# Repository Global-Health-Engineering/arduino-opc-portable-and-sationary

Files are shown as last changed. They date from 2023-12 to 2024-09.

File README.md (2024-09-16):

# Portable and Stationary PM Monitors using Arduino UNO and Alphasense OPC-N3

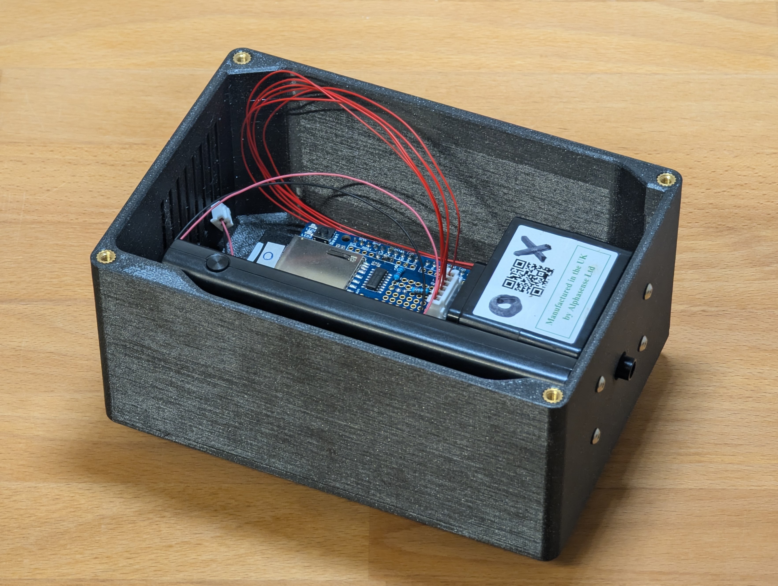
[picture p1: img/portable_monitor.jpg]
portable_monitor


## 1. Overview

This repository provides instructions for the building of particulate matter monitoring systems using the Arduino UNO and Alphasense OPC-N3 optical particle counter module.

There are two variants:

- A portable monitor to measure the personal exposure to particulate matter.
- A stationary monitor for remote long(er)-term deployment.

This repository is part of a bachelor's thesis whose goal it was to develope adaptable low-cost PM monitors and provide a simple and free guide for others also looking to build such systems. The monitors described in this repository can either be copied directly or used as the basis for custom units adapted to specific needs. The project itself is licensed under the the [`CC-BY 4.0`](LICENSE.md) license, however some of the software libraries used are come with different licenses. For more details on this, see [`Section 3`](#3-software-library-licensing) of this README file.

### 1.1. System Overview

The core of both the portable and stationary monitors is a stack made up of an Arduino UNO and an Adafruit Data Logger Shield (DLS). The stationary monitor also includes a DFRobot SIM7600CE-T shield for wireless data transmission to Google Drive. Both monitors feature local data storage on an SD card and proper timestamping using the DLS' real-time clock. To interface with the Alphasense OPC-N3 module, a voltage divider is required to drop the SPI lines from 5 V to 3 V. The handy prototyping area of the DLS is used to implement this and also to host all of the required connectors for power, communication and (optional) status LEDs.

--TODO IMAGE_PORTABLE_SCHEMATIC_OVERVIEW

--TODO IMAGE_STATIONARY_SCHEMATIC_OVERVIEW

### 1.2. Cost breakdown

One goal of the project was to keep the cost of the monitors low, so they are built from readily available and affordable components. The only real exception is the Alphasense OPC-N3. This is rather pricey but could be substituted by a cheaper sensor module if not all of its particular functionality is needed (be aware, replacing the OPC migth require changing the hardware and software interface).

The following tables give a rough breakdown of the costs of each of the monitors. The links are for reference only as sourcing the parts locally is most likely the cheapest option!

#### Cost breakdown of the portable monitor.

| Name                                   | Source                                                                                                         | Approx. price (CHF)    |
| -------------------------------------- | -------------------------------------------------------------------------------------------------------------- | ---------------------: |
| Arduino UNO (R3/R4 Minima)             | [Mouser](https://www.mouser.ch/ProductDetail/Arduino/ABX00080?qs=ulEaXIWI0c9tbG%2FHj5EzRA%3D%3D)               | 20.-                   |
| Adafruit Data Logger Shield (Rev. C)   | [Mouser](https://www.mouser.ch/ProductDetail/Adafruit/1141?qs=GURawfaeGuAe9uOWyGs1aw%3D%3D)                    | 15.-                   |
| SD card (32 GB)                        | [Mouser](https://www.mouser.ch/ProductDetail/SanDisk/SDSDAA-032G?qs=EgF7oUuTQmpUPFrDZtLtsQ%3D%3D)              | 20.-                   |
| RTC battery (CR1220)                   | [Digitec](https://www.digitec.ch/en/s1/product/energizer-cr1220-lithium-1-pcs-cr1220-40-mah-batteries-8762860) | 5.-                    |
| Powerbank                              | [Digitec](https://www.digitec.ch/en/s1/product/sbs-power-bank-10000-mah-5-w-37-wh-powerbanks-19791017)         | 35.-                   |
| Alphasense OPC-N3                      | N/A                                                                                                            | ~500.-                 |
| Small components (LEDs, resistors, wires, etc.) | N/A                                                                                                   | ~10.-                  |
| **Total**                              |                                                                                                                | ~570.-                 |

#### Cost breakdown of the stationary monitor.

| Name                                   | Source                                                                                                                        | Approx. price (CHF)    |
| -------------------------------------- | ----------------------------------------------------------------------------------------------------------------------------- | ---------------------: |
| Arduino UNO (R3/R4 Minima)             | [Mouser](https://www.mouser.ch/ProductDetail/Arduino/ABX00080?qs=ulEaXIWI0c9tbG%2FHj5EzRA%3D%3D)                              | 20.-                   |
| Adafruit Data Logger Shield (Rev. C)   | [Mouser](https://www.mouser.ch/ProductDetail/Adafruit/1141?qs=GURawfaeGuAe9uOWyGs1aw%3D%3D)                                   | 15.-                   |
| SD card (32 GB)                        | [Mouser](https://www.mouser.ch/ProductDetail/SanDisk/SDSDAA-032G?qs=EgF7oUuTQmpUPFrDZtLtsQ%3D%3D)                             | 20.-                   |
| RTC battery (CR1220)                   | [Digitec](https://www.digitec.ch/en/s1/product/energizer-cr1220-lithium-1-pcs-cr1220-40-mah-batteries-8762860)                | 5.-                    |
| Alphasense OPC-N3                      | N/A                                                                                                                           | ~500.-                 |
| UPS board                              | Aliexpress                                                                                                                    | ~5.-                   |
| UPS batteries (2x 18650)               | [Digitec](https://www.digitec.ch/en/s1/product/samsung-lithium-ion-battery-type-18650-1-pcs-18650-285-mah-batteries-16208254) | 30.-                   |
| DFRobot SIM7600CE-T                    | [Mouser](https://www.mouser.ch/ProductDetail/DFRobot/TEL0124?qs=17u8i%2FzlE88MEbXRJuYFsA%3D%3D)                               | 60.-                   |
| Small components (LEDs, resistors, wires, etc.) | N/A                                                                                                                  | ~15.-                  |
| **Total**                              |                                                                                                                               | ~670.-                 |

The cost breakdowns do **NOT** include housings for the monitors, as this is very dependant on the exact use case. They could be as simple as a plastic food container. For this project, the housings were 3D-printed on a consumer grade FDM printer. More details on these can be found in [`Section 1.3.`](#13-3d-printed-housings) of this README file.

### 1.3. 3D-Printed Housings

The files for the 3D-printed housings can be found in the [`cad`](cad) directory. This also contains some simplified CAD models of the UNO and OPC to allow you to design your own housings.

The designs provided can be printed on standard consuer grade FDM printers. They should be printed from a material such as PETG or ASA to make sure they are strong enough and not easily damaged by UV radiation.

#### 1.3.1. Portable Monitor Housing

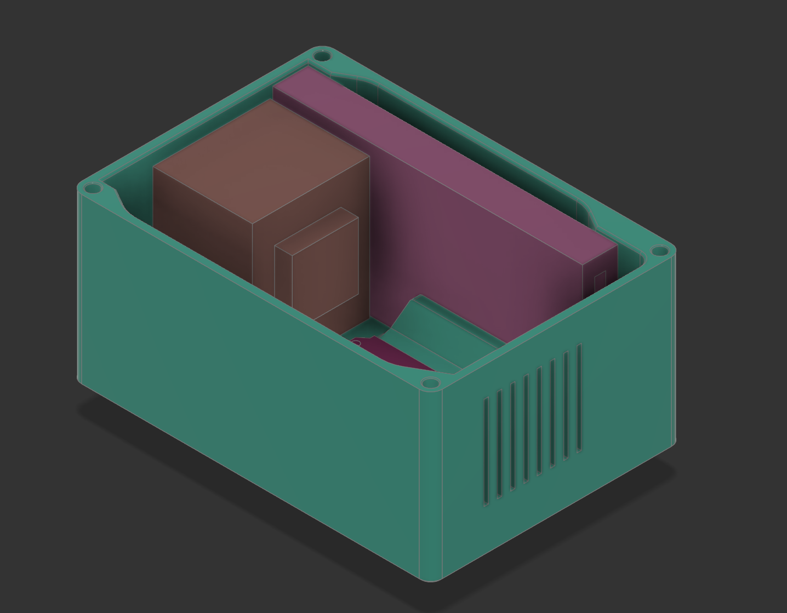
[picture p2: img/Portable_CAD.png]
Portable housing


The housing for the portabel monitor is designed to be used with a GoPro 'Chesty' chest harness. This allows the monitor to be worn somewhat comfortably.

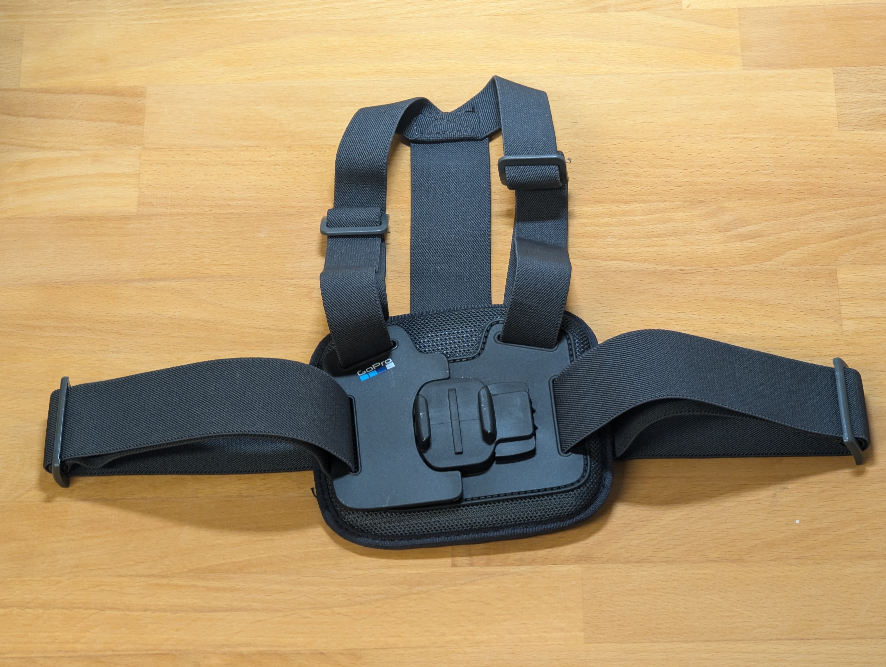
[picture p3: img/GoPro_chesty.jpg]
GoPro_chesty


A list of all the hardware required for the portable monitor housing is provided below.

#### Parts List of the Portable Monitor Housing

| Item                | Note        | Quantity       |
| ------------------- | ----------- | :------------: |
| 3D-printed parts    | PETG or ASA | 1 complete set |
| Threaded inserts M3 | -           | 7              |
| Threaded inserts M4 | -           | 8              |
| M3x8 screws         | button head | 7              |
| M3x10 screws        | button head | 7              |
| M3x16 screws        | button head | 2              |
| M4x10 screws        | button head | 8              |
| GoPro 'Chesty'      | -           | 1              |

#### 1.3.2. Stationary Monitor Housing

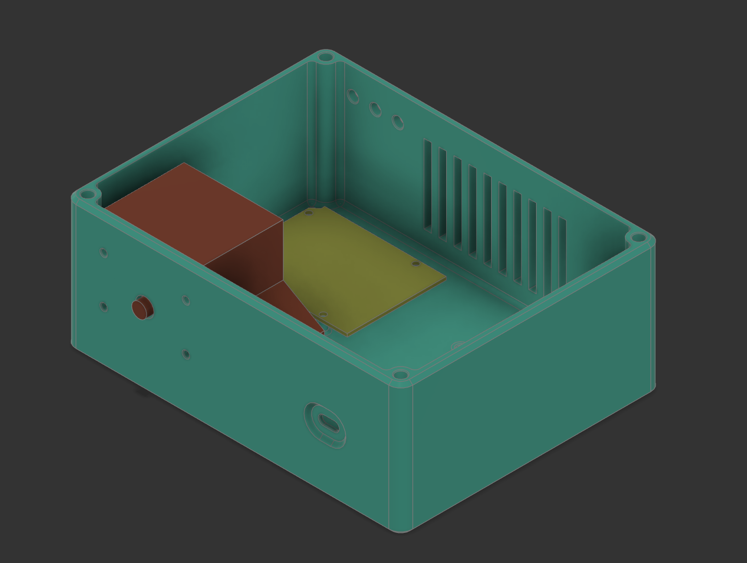
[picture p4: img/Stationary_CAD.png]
Stationary housing


A list of all the hardware required for the stationary monitor housing is provided below.

#### Parts List of the Portable Monitor Housing

| Item                | Note        | Quantity       |
| ------------------- | ----------- | :------------: |
| 3D-printed parts    | PETG or ASA | 1 complete set |
| Threaded inserts M3 | -           | 8              |
| Threaded inserts M4 | -           | 4              |
| M3x8 screws         | button head | 8              |
| M3x10 screws        | button head | 4              |
| M4x12 screws        | countersunk | 4              |
| M3x20 standoffs     | male/female | 4              |

## 2. Instructions

To build your own PM monitors, first follow the assembly guide for you chosen version. To use you monitors, have a look at the usage guides. These can be found in the [`docs`](docs) directory. Alternatively, the table below provides direct links to individual guides.

| Portable                                | Stationary                                |
| :-------------------------------------: | :---------------------------------------: |
| [`Assembly`](docs/portable_assembly.md) | [`Assembly`](docs/stationary_assembly.md) |
| [`Usage`](docs/portable_usage.md)       | [`Usage`](docs/stationary_usage.md)       |

## 3. Software Library Licensing

The code provided in this repository makes use of the libraries listed in the following table. When using any code from this repository, make sure you follow any applicable licenses of the libraries in addition to the license of the project. A copy of the licenses is provided in the [`licenses`](licenses) directory.

| Library | License |
| ------- | ------- |
| [SPI.h](https://github.com/arduino/ArduinoCore-avr/tree/master/libraries/SPI)                     | `LGPL v2.1` |
| [SD.h](https://github.com/arduino-libraries/SD)                                                   | `GPL v3`    |
| [RTClib](https://github.com/adafruit/RTClib)                                                      | `MIT`       | 
| [SoftwareSerial](https://github.com/arduino/ArduinoCore-avr/tree/master/libraries/SoftwareSerial) | `LGPL v2.1` |

## 4. Change Log

## Tree --TODO UPDATE

    .
    ├── CITATION.cff
    ├── LICENSE.md
    ├── README.md
    ├── cad
    │   ├── Portable
    │   │   ├── Portable_v1-0-0.f3d
    │   │   ├── Portable_v1-0-0.step
    │   │   ├── Portable_v1-0-0.stl
    │   │   └── test.stl
    │   ├── README.md
    │   ├── Stationary
    │   │   ├── Stationary_v1-0-0.f3d
    │   │   ├── Stationary_v1-0-0.step
    │   │   └── Stationary_v1-0-0.stl
    │   └── misc
    │       ├── Alphasense_OPC-N3.f3d
    │       ├── Alphasense_OPC-N3.step
    │       ├── Arduino_UNO_PCB.f3d
    │       ├── Arduino_UNO_PCB.step
    │       ├── SBS_TTBB1000FASTA.f3d
    │       └── SBS_TTBB1000FASTA.step
    ├── img
    │   ├── Portable_CAD.png
    │   ├── README.md
    │   └── Stationary_CAD.png
    └── src
        ├── Data_Reception
        │   └── Google_Sheet_Script.txt
        ├── Portable_v1-0-0
        │   └── Portable_v1-0-0.ino
        ├── Portable_v2-0-0
        │   └── Portable_v2-0-0.ino
        ├── README.md
        ├── RTC_adjust
        │   ├── README.md
        │   └── RTC_adjust_v1-0-0.ino
        └── Stationary
            ├── README.md
            └── Stationary_v1-0-0.ino

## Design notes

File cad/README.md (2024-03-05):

# cad

This directory contains 3D CAD models of the monitor housings and components.

## Portable & Stationary

These subdirectories contain 3D-printable housings for the monitors (portable monitor & stationary monitor).

For the bill of materials check the main `README.md` file.

The `.stl` files can be directly imported into the slicing software. They are designed to be printed on an FDM printer using a 0.4 mm nozzle.  
To print the parts, split the mesh into seperate parts.

## misc

This subdirectory contains very basic placeholder models of the components that were used to design a custom enclosure.

---

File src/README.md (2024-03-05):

# src

This directory contains the source code for Arduino and for receiving data sent by Arduino.

    .
    ├── Data_Reception
    │   └── Google_Sheet_Script.txt
    ├── Portable_v1-0-0
    │   └── Portable_v1-0-0.ino
    ├── Portable_v2-0-0
    │   └── Portable_v2-0-0.ino
    ├── README.md
    ├── RTC_adjust
    │   ├── README.md
    │   └── RTC_adjust_v1-0-0.ino
    └── Stationary
        ├── README.md
        └── Stationary_v1-0-0.ino

| name | description |
| - | - |
| `Google_Sheet_Script.txt` | Google Sheets script for pulling data from the stationary monitor |
| `Portable_v1-0-0.ino` | ? |
| `Portable_v2-0-0.ino` | Code for the portable monitor. |
| `RTC_adjust_v1-0-0.ino` | Code for adjusting the RTC on Adafruit DLS |
| `Stationary_v1-0-0.ino` | Code for the stationary monitor. |

## Portable monitor

The microcontroller for portable monitoring collects data from the Alphasense OPC-N3 every *XXX* seconds and stores it on the SD card.
Its runtime on a *XXX* mAh battery is *XXX* hours.

## Stationary monitor

The microcontroller for portable monitoring collects data from the Alphasense OPC-N3 every *XXX* seconds and stores it on the SD card.

In normal operation, the system runs connected to the electrical grid. However, it switches without interruption to the battery power supply once the grid is down.

It sends data to the cloud though 2G/3G/4G communication every *XXX* min(hours?). The communication shield is switched off when not used to limit power consumption.

---

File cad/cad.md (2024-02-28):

# cad

This directory contains 3D CAD models of the monitor housings and components.

## Portable/Stationary

3D-printable housings for the monitors. For the bill of materials check the main `README.md` file.

Designed to be printed on an FDM printer using a 0.4 mm nozzle. The `.stl` files can be directly imported into the slicing software.  
To print the parts, split the mesh into seperate parts.

## misc

Very basic placeholder models of the components that can be used to design a custom enclosure.

---

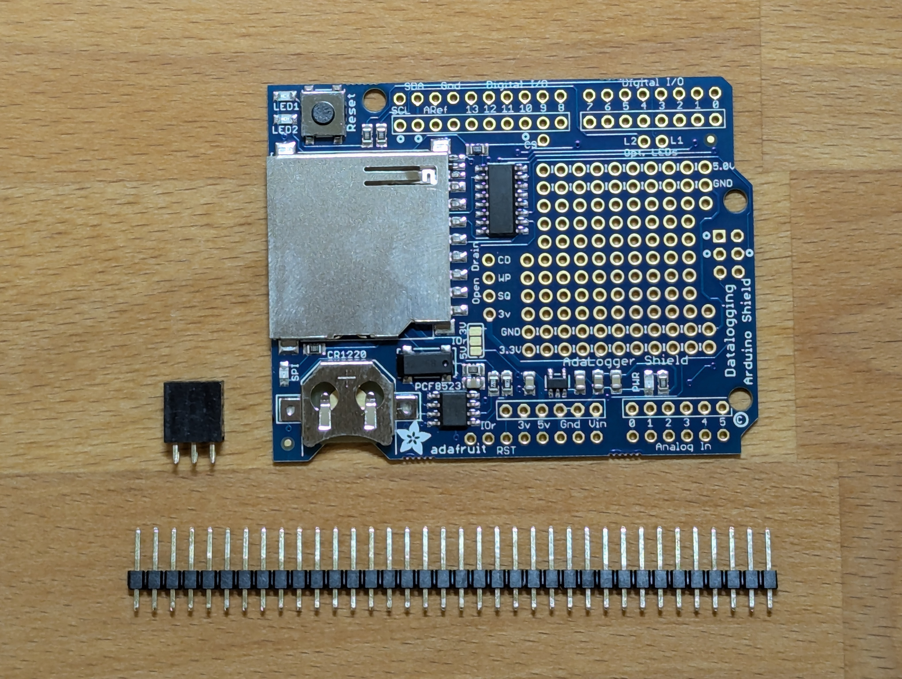
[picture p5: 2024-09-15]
img/DLS.jpg

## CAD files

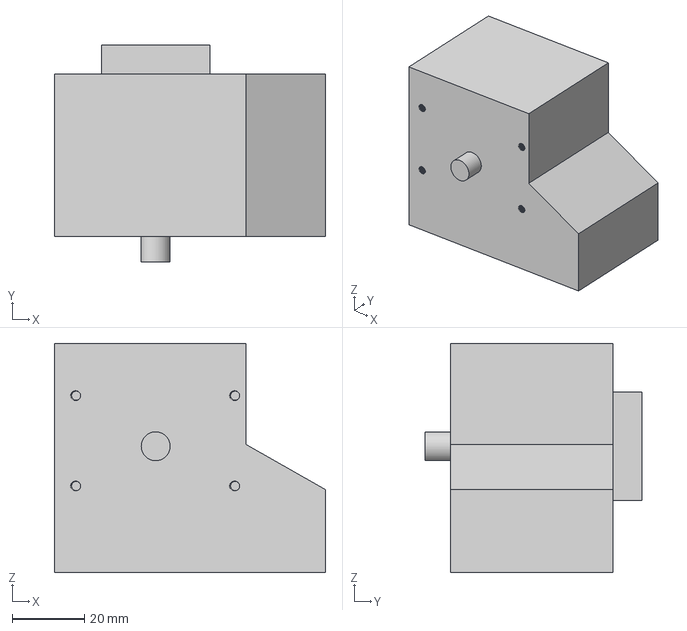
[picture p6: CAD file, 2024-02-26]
cad/misc/Alphasense_OPC-N3.step
75.0 x 60.0 x 63.5 mm

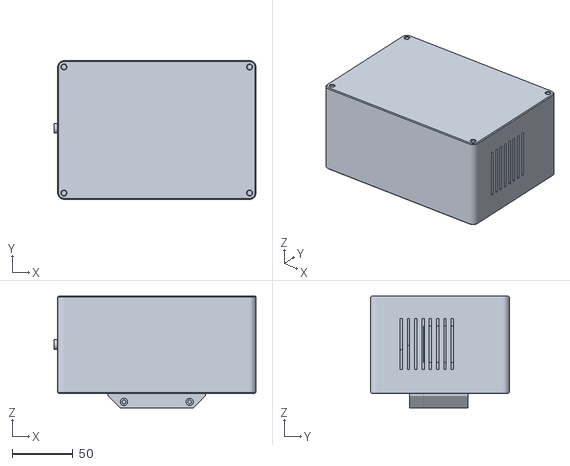
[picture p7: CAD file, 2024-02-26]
cad/Portable/Portable_v1-0-0.stl
166.0 x 114.0 x 92.0

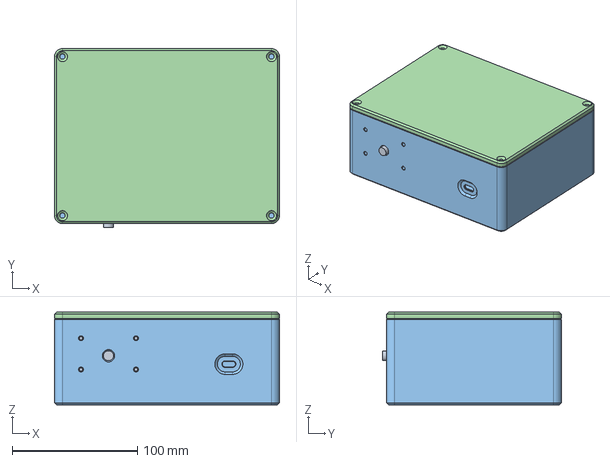
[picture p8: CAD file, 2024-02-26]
cad/Stationary/Stationary_v1-0-0.step
180.0 x 143.0 x 74.0 mm
Alphasense_OPC-N3 v3
Arduino_UNO_PCB v4

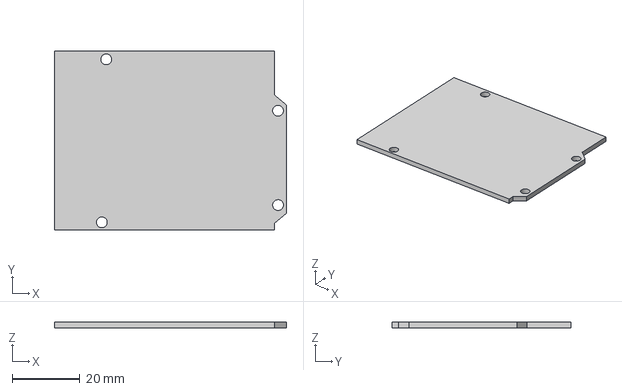
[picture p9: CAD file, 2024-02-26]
cad/misc/Arduino_UNO_PCB.step
68.6 x 53.0 x 1.70 mm

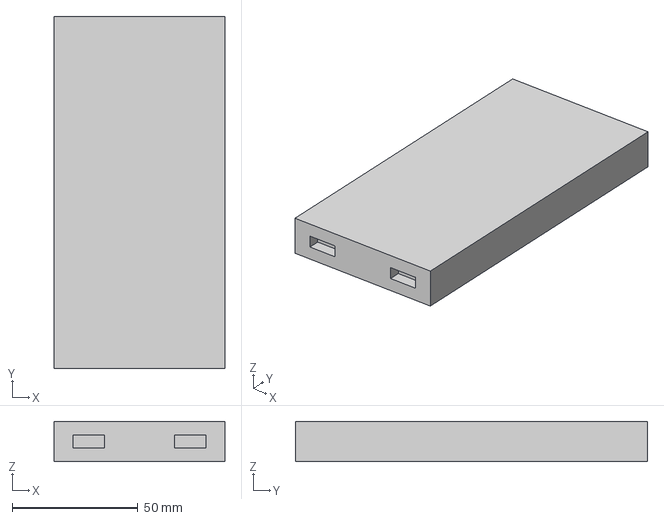
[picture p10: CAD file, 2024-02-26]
cad/misc/SBS_TTBB1000FASTA.step
68.0 x 140.0 x 16.0 mm

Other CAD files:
cad/Portable/Portable_v1-0-0.f3d
cad/Stationary/Stationary_v1-0-0.f3d
cad/Stationary/Stationary_v1-0-0.stl
cad/misc/Alphasense_OPC-N3.f3d
cad/misc/Arduino_UNO_PCB.f3d
cad/misc/SBS_TTBB1000FASTA.f3d

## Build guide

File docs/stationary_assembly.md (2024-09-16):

# Assembly of the Stationary Monitor

The assembly of the stationary monitor core is a bit more involved than that of the portable one. The main reason for this is a pin conflict between the Adafruit DLS and the DFRobot SIM shield. Other than this, the process is very similar to that of the portable monitor.

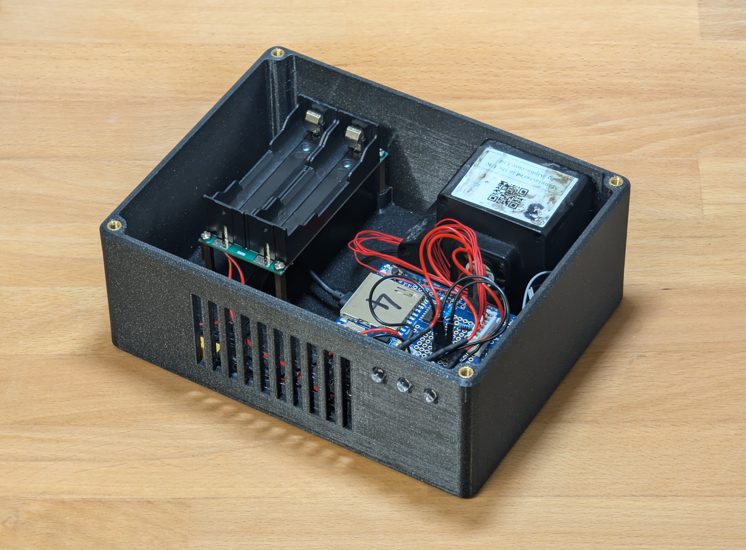
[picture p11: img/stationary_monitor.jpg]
stationary_monitor


#### Parts List

| Item                    | Value/note               | Quantity              |
| ----------------------- | ------------------------ | :-------------------: |
| Arduino UNO             | R3/R4 Minima             | 1                     |
| Adafruit DLS            | Rev. C                   | 1                     |
| Headers for DLS         | included w/ DLS          | 1 complete set        |
| DFRobot SIM7600CE-T     | w/ stacking headers      | 1                     |
| SIM card                | w/ data subscription     | 1                     |
| Wire-to-board connector | 2 pin                    | 1 set (male & female) |
| Wire-to-board connector | 6 pin                    | 1 set (male & female) |
| USB cable               | type matching powerbank  | 1                     |
| OPC connector/cable     | 6 pin Molex Pico-Clasp   | 1 (male)              |
| Resistor                | $2'200 \ \Omega$         | 1                     |
| Resistor                | $3'300 \ \Omega$         | 1                     |
| Wire                    | $0.25 \ \textrm{mm}^2$   | 4 colours             |
| LEDs                    | $3$ or $5 \ \textrm{mm}$, w/ resistors for $5 \ \textrm{V}$ | 3 (green, red, blue)  |
| LED headers             | 3 pin                    | 2 (matching LEDs)     |
| CR1220 battery          | -                        | 1                     |
| SD card                 | max. $32 \ \textrm{GB}$, FAT formatted  | 1                     |

- For the wire-to-board connectors on the DLS, any type with a pitch of $\sim 2.5 \ \textrm{mm}$ works. JST XH connectors are a good choice as they are pretty resistant aginst pull out and fairly compact. Alternatively, the wires _could_ be soldered directly to the DLS, skipping the use of connectores, however this is not recommended as it makes swapping any component a lot more work.

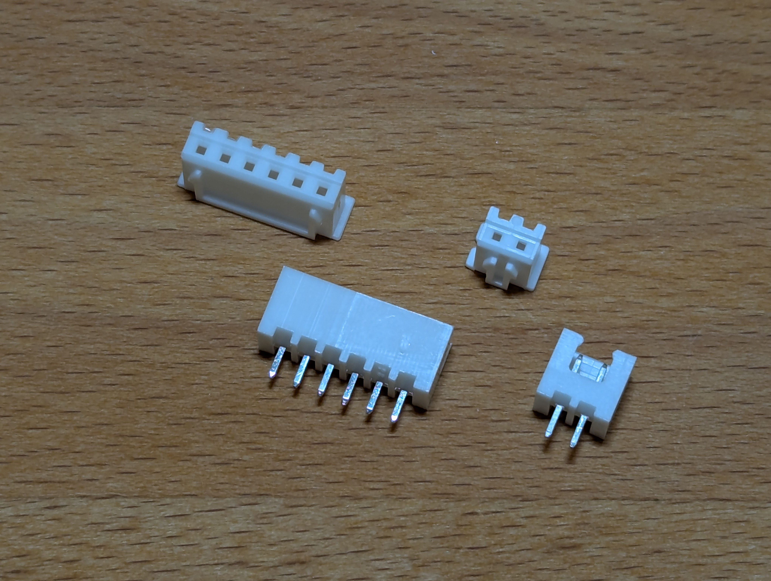
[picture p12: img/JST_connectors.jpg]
JST_connectors


- For the OPC you need a 6 pin Molex Pico-Clasp connector. This is a _tiny_ connector and you should ideally use a special (and expensive) crimping tool to properly crimp these pins. It is easier to buy a [pre-crimped cable](https://www.aliexpress.com/item/1005005897060590.html) set which already has the connector on one side.

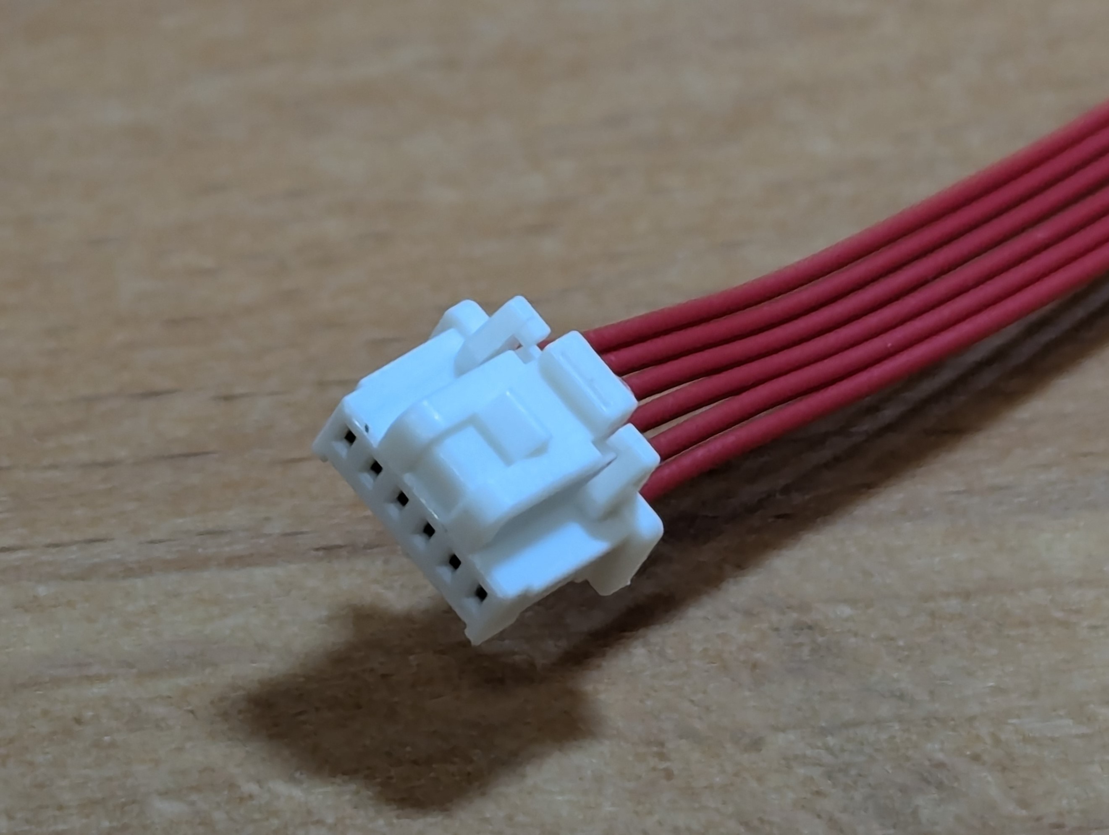
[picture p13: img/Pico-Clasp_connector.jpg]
Pico-Clasp_connector


- For the external status LED headers, any type with a pitch of $\sim 2.5 \ \textrm{mm}$ works. Pin headers ("DuPont") are a good choice for this application. You can either solder male pin headers to the DLS and crimp female connectors to the LEDs or vice versa. Alternatively, the wires _could_ be soldered directly to the DLS, skipping the use of connectores, however this is not recommended as it makes working on the monitor a lot more work.

### Required Tools

- Soldering iron
- Solder (ideally lead-free)
- PPE (safety glasses/goggles and mask/respirator)
- Wire cutters
- Wire strippers
- Crimping tool (appropriate version for the chosen connectors)
- Pliers
- Multimeter

Additionally, a soldering stand (third hand) is really helpful but not absolutely necessary.

## Step 1: Assembling the DLS

For the assembly of the DLS, first follow `Step 1` in the [assembly guide of the portable monitor](portable_assembly.md), skipping `Step 1.4`. If you already soldered the onboard LEDs, don't worry as tis won't prevent the external ones from working.

### Step 1.5: Soldering the External LED Headers (optional)

To facilitate the connection of external status LEDs, headers are soldered to pins `5`, `6` and `7` as well as to the `GND` row on the DLS.

- If you are using female pin headers, you will first have to split off the required amount of pins. You need two strips with 3 pins each. The easiest way to achieve this for female headers is to first pull out the connector "forks" from the bottom with a pair of pliers.

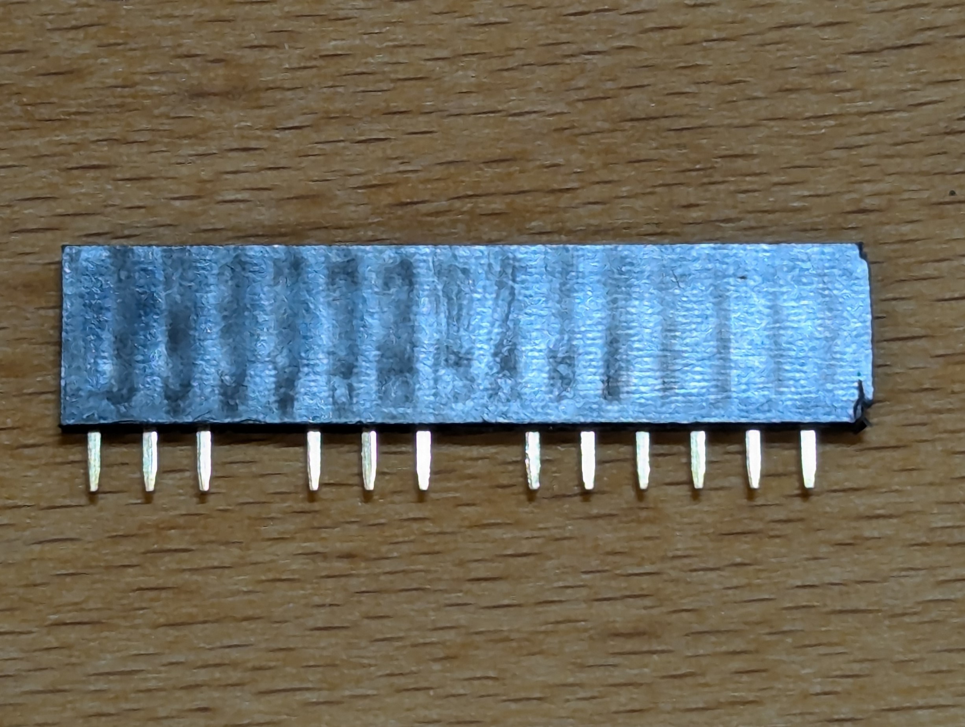
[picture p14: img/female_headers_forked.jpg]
female_headers_forked


- Then you can repeatedly score the plastic housing along the pin you removed until you can snap off the desired amount of pins.

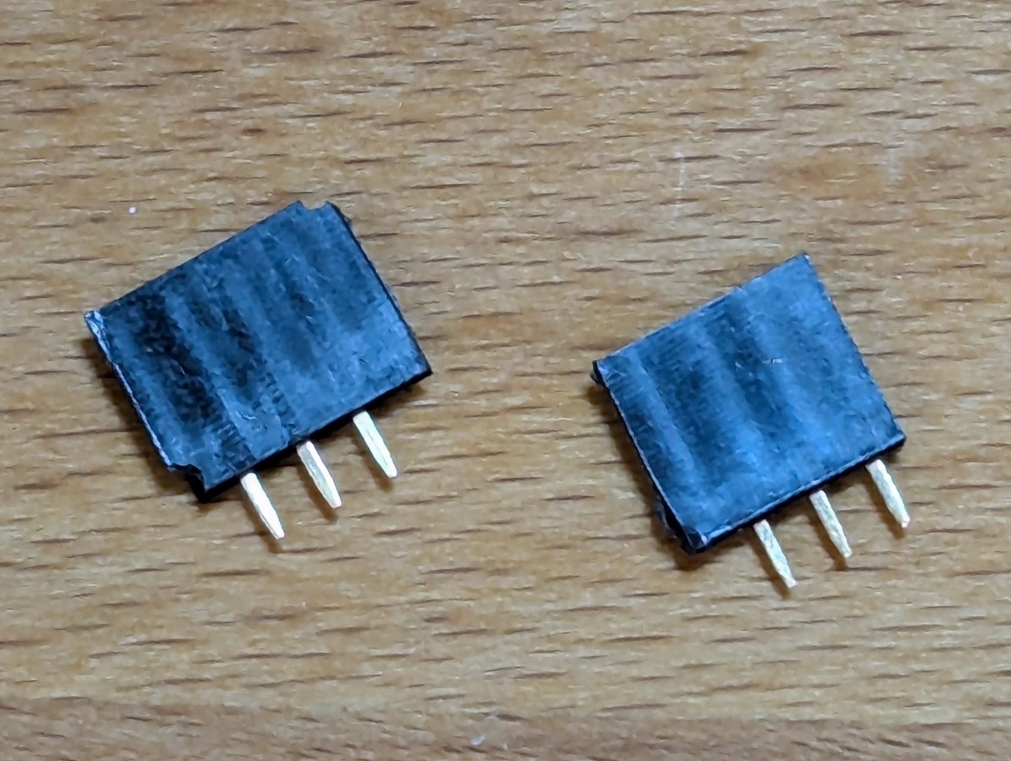
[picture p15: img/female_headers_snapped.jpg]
female_headers_snapped
 

- Finally, sand the trimmed edges of the headers smooth.

 - Place one of the headers as shown in the photo below and solder it to the DLS. Note that it is placed on the pins labeled `5`, `6` and `7`.

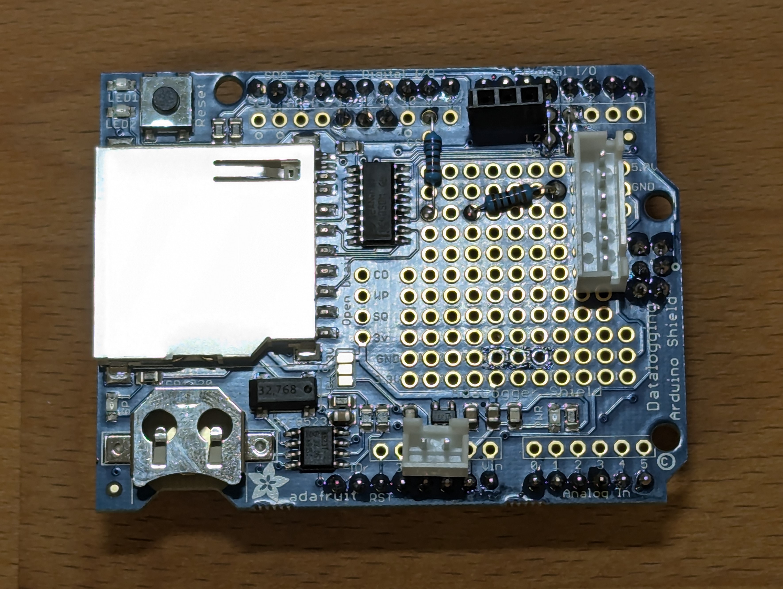
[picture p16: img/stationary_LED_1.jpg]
stationary_LED_1


- Finally, place the remaining header as shown in the photo below. Note that it is positioned on the `GND` row of the DLS. The exact positioning along this row doesn't matter.

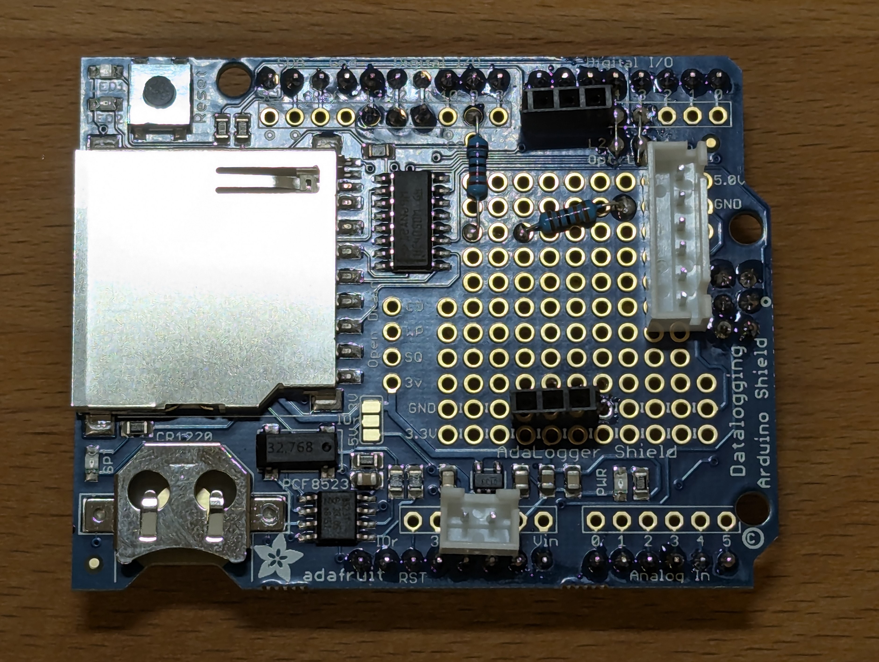
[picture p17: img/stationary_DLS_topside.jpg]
stationary_LED_2


Your DLS is now complete and should look like the one in the photos below.

stationary_DLS_topside

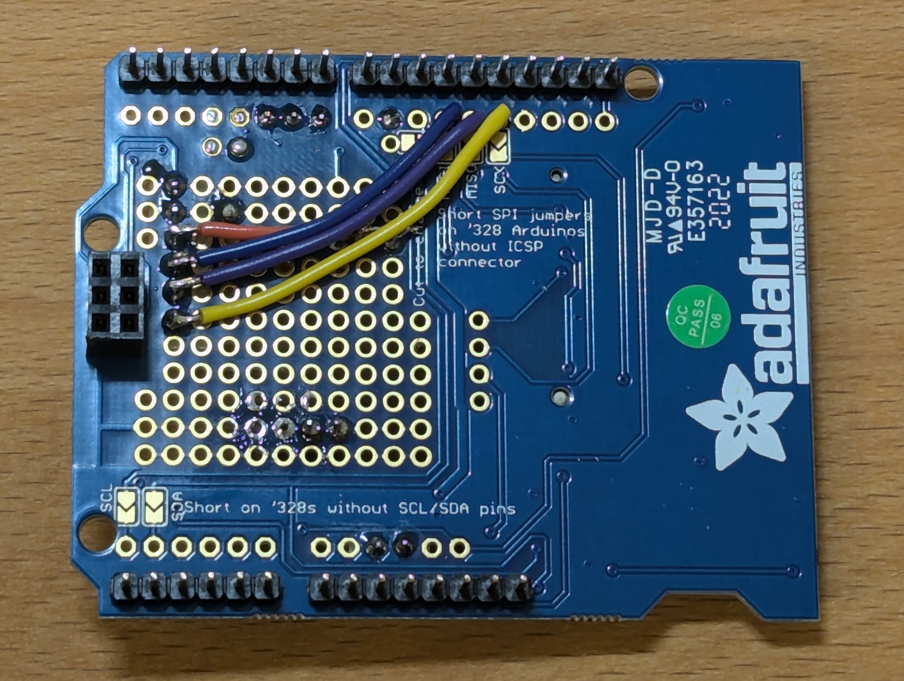
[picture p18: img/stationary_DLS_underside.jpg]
stationary_DLS_underside


## Step 2: Preparing the Power Cables

The stationary monitor needs two power cables, one for the UNO and one for the SIM shield.

- Cut two lenghts of wire and crimp JST connector pins to one end of each. The lengths of these ares dependant on the location and orientation of the components in your chosen housing.

- Cut off the Micro-USB connector of an old USB cable. The length of this is dependant on the location and orientation of the components in your chosen housing. If the cable is too short you can lengthen it by soldering on lengths of additional wire.

- Strip the cut end of the USB cable to expose the individual wires inside. You should see four wires: white, green, red and black.

- Trim the white and green wires  so they are flush with the insulation of the whole cable.

- Solder the unconnected ends of the four wires to the output terminals of the UPS board as shown in the photo below. Optionally you can include an XT30 or similar connector in the Arduino power cable.

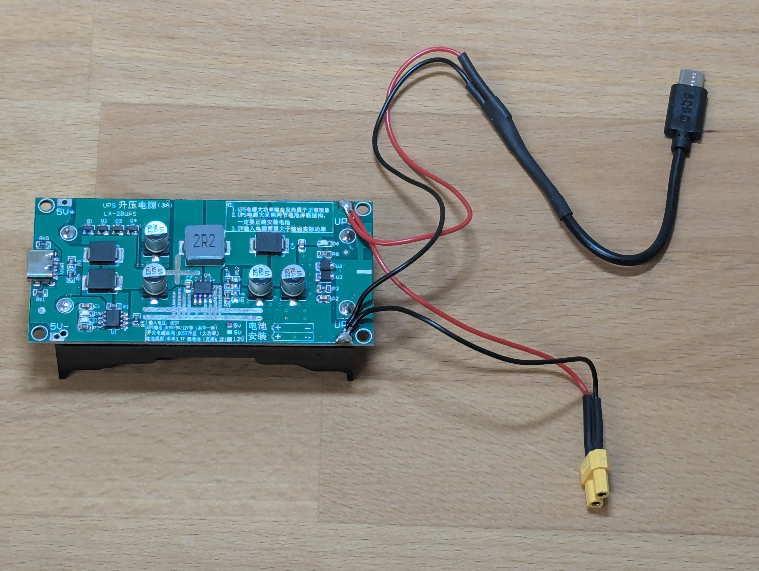
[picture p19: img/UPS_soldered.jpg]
UPS_soldered


- Insert the JST conector pins into their housing as shown in the photo below. Note the orientation of the wires.

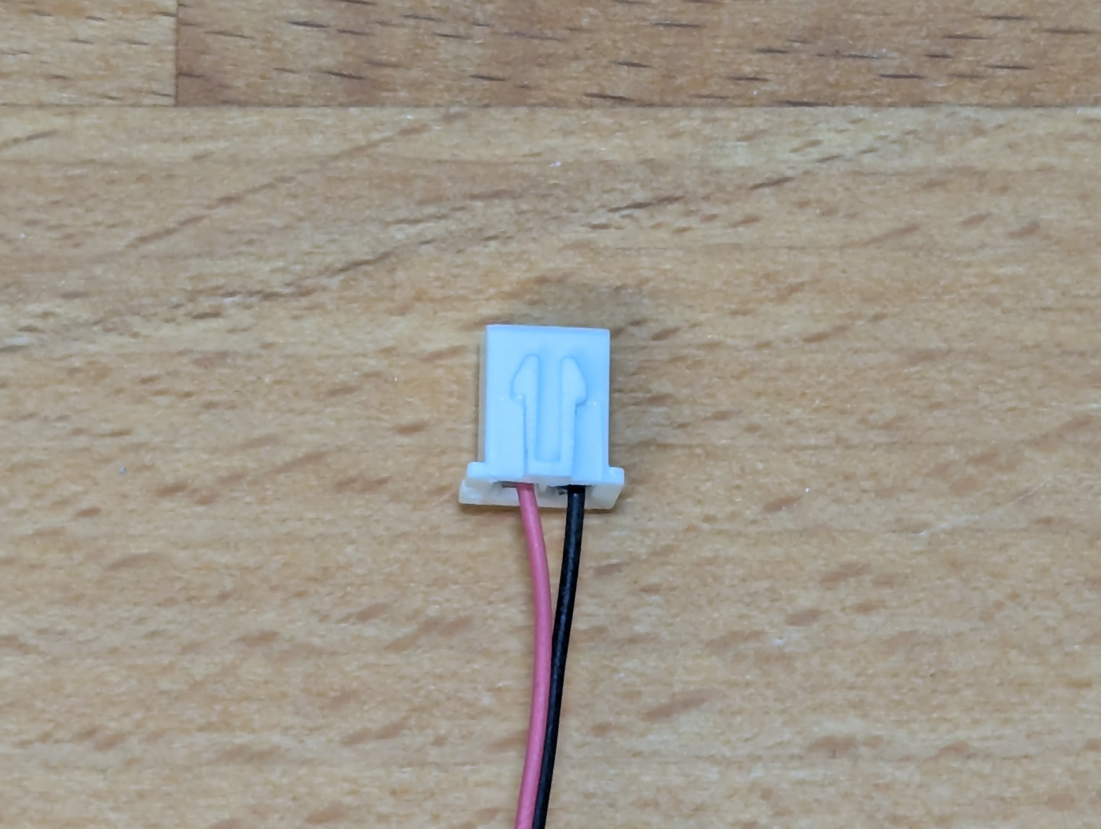
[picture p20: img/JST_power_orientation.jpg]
JST_power_orientation


## Step 3: Preparing the OPC Cable

For the assembly of the OPC cable, follow `Step 3` in the [assembly guide of the portable monitor](portable_assembly.md).

## Step 4: Replacing the UNO's Headers

To stack the SIM shield, UNO and DLS in the correct orders, the stacking headers of the SIM shield have to be swapped with the female headers of the UNO.

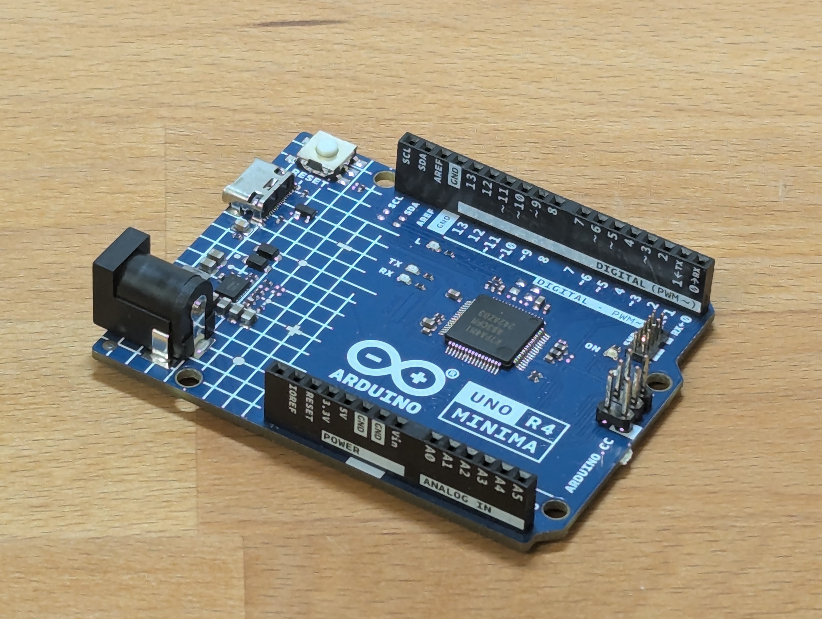
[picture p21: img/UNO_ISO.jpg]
UNO_ISO


- Desolder the stacking headers of the SIM shield and the female headers of the UNO. This can be done by using solder wick to one by one desolder each individual pin. Take your time here and be careful not to overheat the SIM shield or UNO!

- Solder the stacking headers to the UNO. To help keep them aligned you can place the DLS on top.

- Soler the female headers to the SIM shield. To help keep them aligned you can place the UNO or DLS on top.

Your UNO and SIM shield should now look like the ones in the photo below.

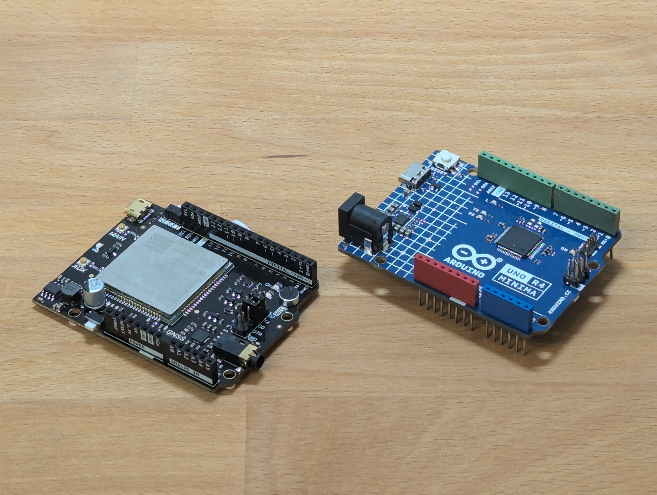
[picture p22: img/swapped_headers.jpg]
swapped_headers


## Step 5: Soldering the SIM Shield Jumper Wire

To avoid a pin conflict between the DLS and the SIM shield, a pin on the UNO needs to be clipped and a small jumper wire soldered to the SIM shield.

- Clip pin `12` of the stacking headers on the underside of the UNO as shown in the photo below.

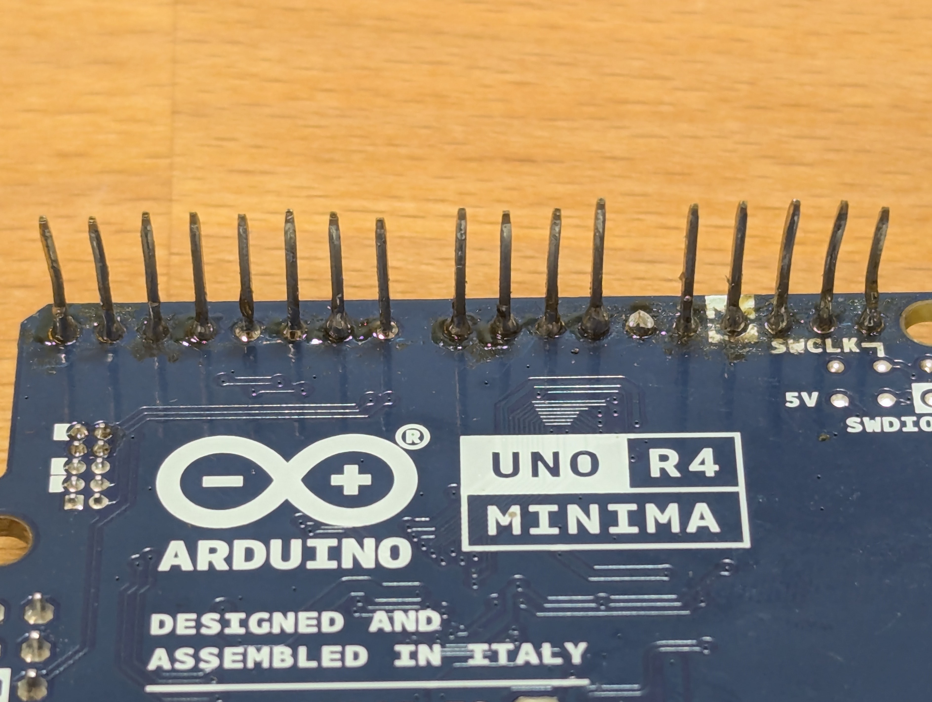
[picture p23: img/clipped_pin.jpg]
clipped_pin
  

- Solder a small length of wire to the SIM shield as shown in the photo below. Note that it connects pins `8` and `12`.

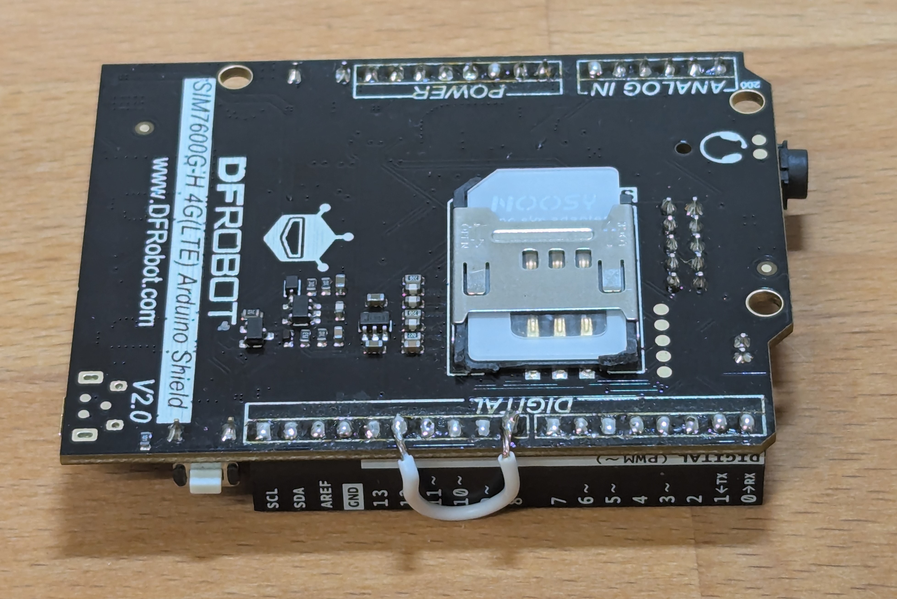
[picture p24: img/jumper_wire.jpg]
jumper_wire


## Step 6: Putting it all together

- Make sure you have the jumpers on the SIM shield set as shown in the photo below.

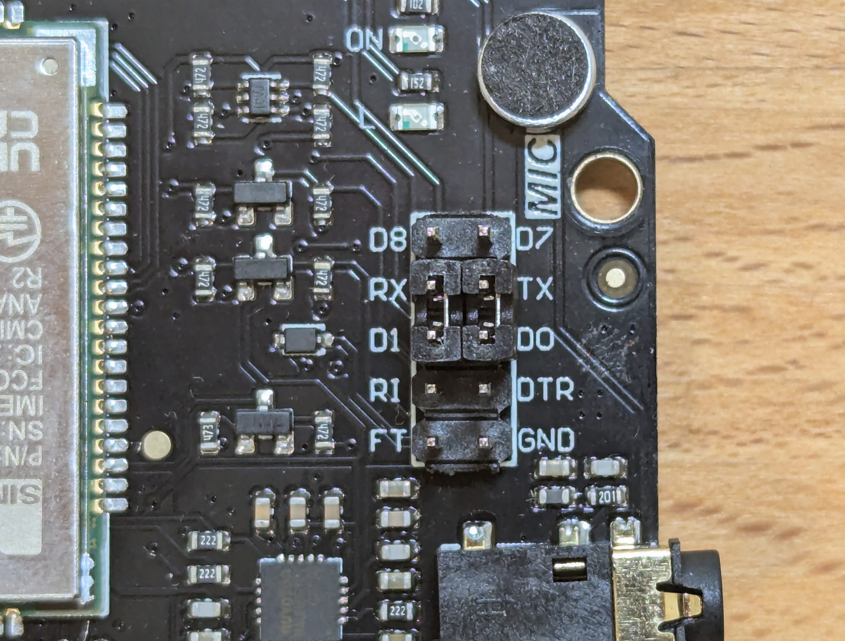
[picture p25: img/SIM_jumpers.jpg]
SIM_jumpers


- With the DLS, power and OPC cables and the SIM shield prepared, take the Arduino UNO and place it ontop of the SIM shield. Make sure to line up all of the headers correctly and carefully push the UNO down onto the SIM shield.
  
- Repeat this process to place the DLS on top of the UNO.

- Next, insert a CR1220 button cell battery and the SD card into their slots on the DLS and connect the OPC using the 6 pin connector and OPC cable.

- Insert the SIM card into the corresponding slot on the underside of the SIM shield and connect the antenna.

- Do not insert the UPS batteries or connect the UPS to a USB power supply yet. Only do this once the firmware has been fully uploaded and you are ready to start using the monitor.

If you printed the housings, it might be easier to screw the SIM shield onto its mountng spots and to connect the antenna before putting the UNO and DLS on top and to screw in the OPC before connecting its cable to the DLS.

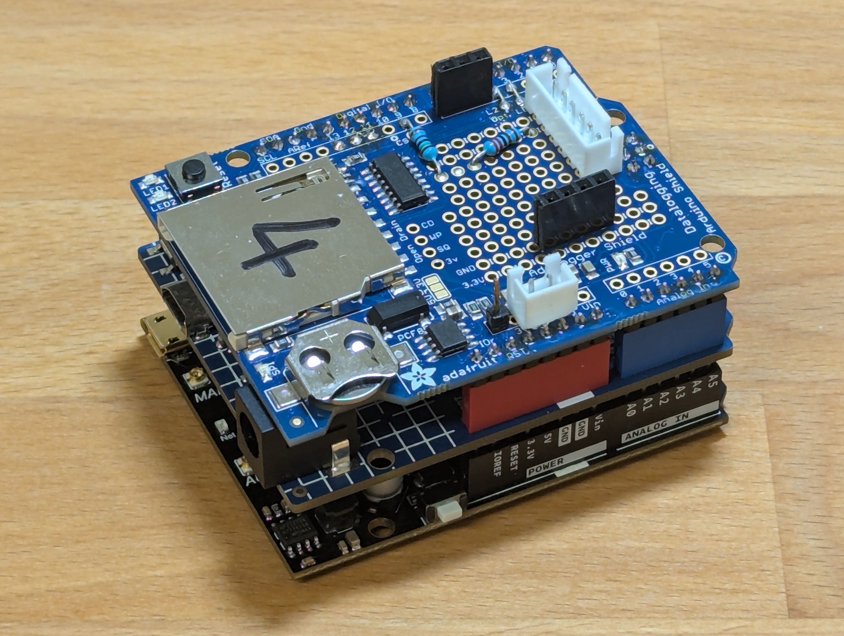
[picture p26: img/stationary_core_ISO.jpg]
stationary_core_ISO


Congratulations, the core of your stationary PM monitor is now fully assembled! Next, keep following the steps below to get it ready for using.

## Step 7: Preparing the Google Drive File --TODO

## Step 8: Adjusting the RTC

For the adjustment of the RTC, follow `Step 5` in the [assembly guide of the portable monitor](portable_assembly.md).

## Step 9: Uploading the Firmware --TODO

- Open the file `Stationary.ino` in the Arduino IDE.

-TOOD replace the following with deeets: SIM, google drive

Phew, you made it! Your stationary PM monitor is now ready to start collecting measurements. Have a look at the [`usage guide`](portable_usage.md) to help you with this.

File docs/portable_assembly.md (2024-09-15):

# Assembly of the Portable Monitor 

The assembly of the portable monitor core is fairly simple thanks to the Adafruit DLS. Only basic soldering skills and a bit of wire crimping are required to complete it.

portable_monitor

#### Parts List

| Item                    | Value/note              | Quantity              |
| ----------------------- | ----------------------- | :-------------------: |
| Arduino UNO             | R3/R4 Minima            | 1                     |
| Adafruit DLS            | Rev. C                  | 1                     |
| Headers for DLS         | included w/ DLS         | 1 complete set        |
| Wire-to-board connector | 2 pin                   | 1 set (male & female) |
| Wire-to-board connector | 6 pin                   | 1 set (male & female) |
| USB cable               | type matching powerbank | 1                     |
| OPC connector/cable     | 6 pin Molex Pico-Clasp  | 1 (male)              |
| Resistor                | $2'200 \ \Omega$        | 1                     |
| Resistor                | $3'300 \ \Omega$        | 1                     |
| Wire                    | $0.25 \ \textrm{mm}^2$  | 4 colours             |
| CR1220 battery          | -                       | 1                     |
| SD card                 | max. $32 \ \textrm{GB}$, FAT formatted | 1                     |

- For the wire-to-board connectors on the DLS, any type with a pitch of $\sim 2.5 \ \textrm{mm}$ works. JST XH connectors are a good choice as they are pretty resistant aginst pull out and fairly compact. Alternatively, the wires _could_ be soldered directly to the DLS, skipping the use of connectores, however this is not recommended as it makes swapping any component a lot more work.

JST_connectors

- For the OPC you need a 6 pin Molex Pico-Clasp connector. This is a _tiny_ connector and you should ideally use a special (and expensive) crimping tool to properly crimp these pins. It is easier to buy a [pre-crimped cable](https://www.aliexpress.com/item/1005005897060590.html) set which already has the connector on one side.

Pico-Clasp_connector

### Required Tools

- Soldering iron
- Solder (ideally lead-free)
- PPE (safety glasses/goggles and mask/respirator)
- Wire cutters
- Wire strippers
- Crimping tool (appropriate version for the chosen connectors)
- Pliers
- Multimeter

Additionally, a soldering stand (third hand) is really helpful but not absolutely necessary.

## Step 1: Assembling the DLS

As the first step, the DLS is populated with all the required components and connectors.  

### Step 1.0: Installing the DLS Headers

This step is only required if you bought a DLS that does not have the headers installed yet. For this step, follow the step `Installing the Headers` in [Adafruit's DLS manual](https://cdn-learn.adafruit.com/downloads/pdf/adafruit-data-logger-shield.pdf).

### Step 1.1: Soldering the Power and OPC Connectors

In this step, the 2 pin power connector and 6 pin connector for the OPC are soldered onto the DLS. 

- First, position the 2 pin power connector as shown in the photo below in the holes labeled `5v` and `GND` and take note of its orientation. 

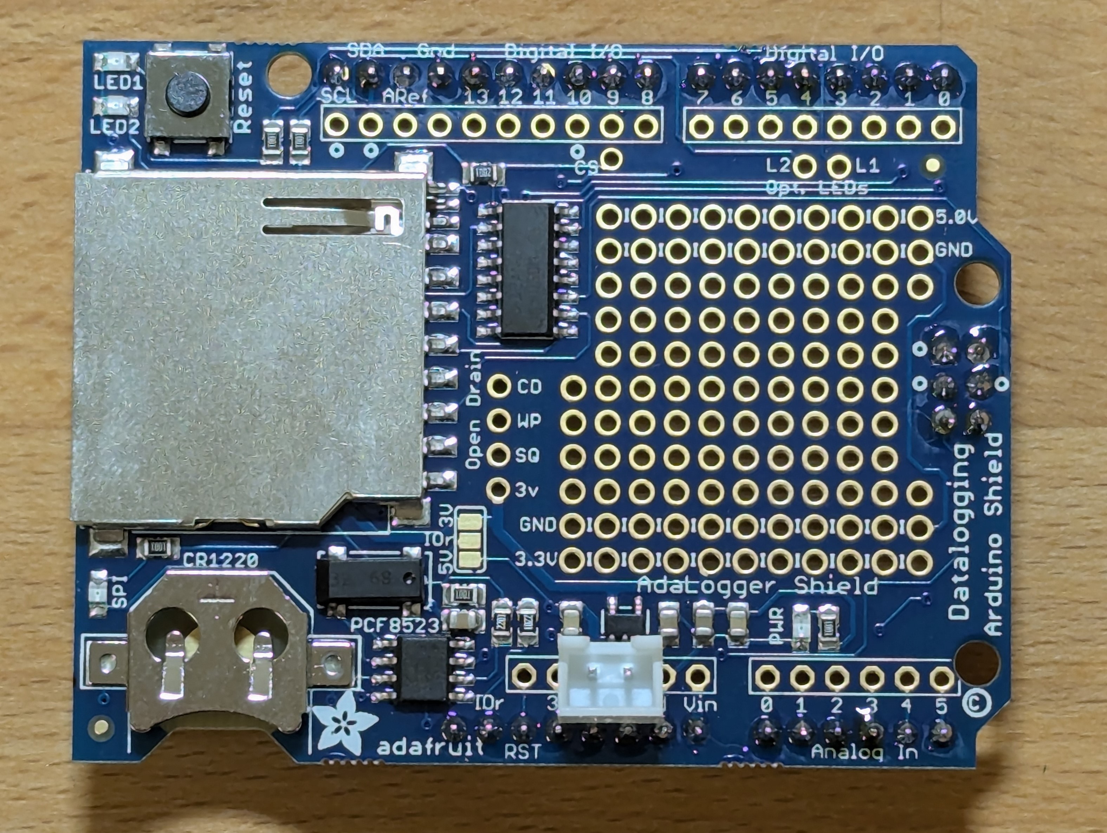
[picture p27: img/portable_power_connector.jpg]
portable_power_connector


- If you're using JST XH connectors you might have to trim a little bit of the plastic housing to clear the tips of the headers on the outside. Do this _very carefully_ with a sharp hobby knife.

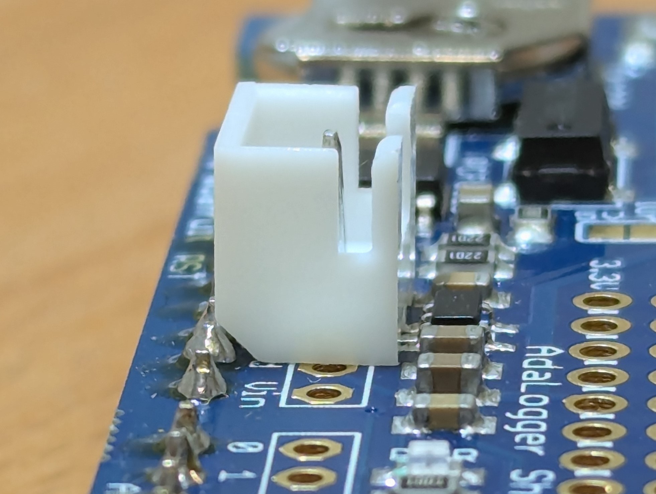
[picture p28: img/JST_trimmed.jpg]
JST_trimmed


- Once the header is positioned, solder it from the underside, ensuring that the pins are not shorted.

- Next, position the 6 pin OPC connector as shown in the photo below. Note that it is positioned so that the two pins towards the edge are on the rows labeled `5.0V` and `GND` and how it is orientated.

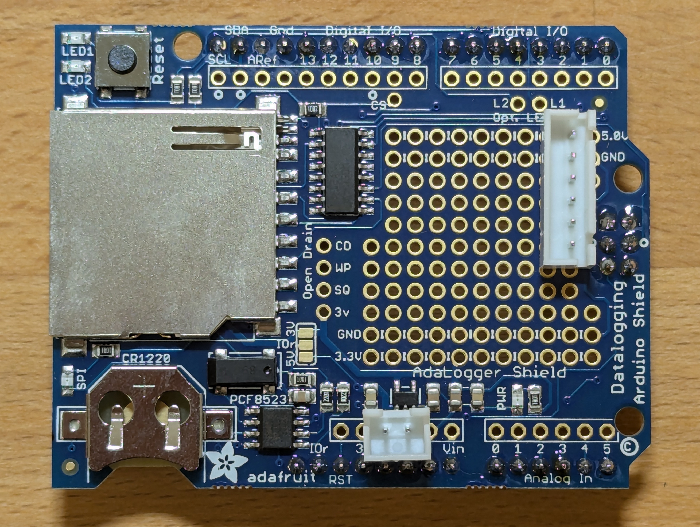
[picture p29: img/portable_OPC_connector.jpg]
portable_OPC_connector


- Again, solder this from the underside, ensuring that no two adjacent pins are shorted.

### Step 1.2: Soldering the Resistors

In this step, the two resistors for the OPC voltage divider are soldered onto the DLS.

- First, take the `2'200 ohm` resistor and bend its legs so that it fits into the holes as shown in the photo below.
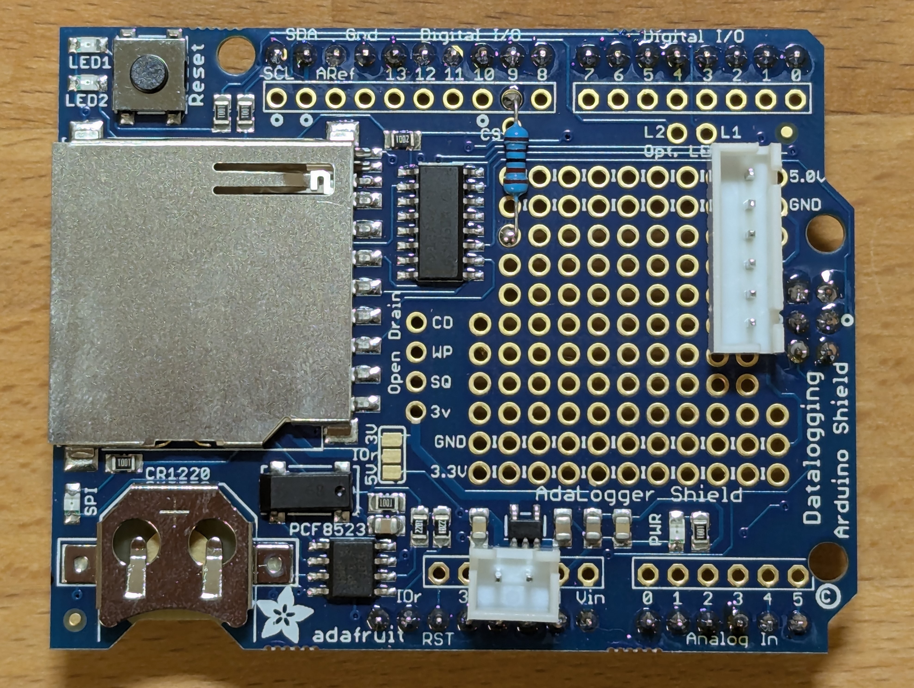
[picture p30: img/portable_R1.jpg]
portable_R1


- Once positioned correctly, solder the resistor from the underside and trim the legs.

- For the `3'300 ohm` resistor, position it as shown in the schematic below and repeat the same process as for the first resistor.

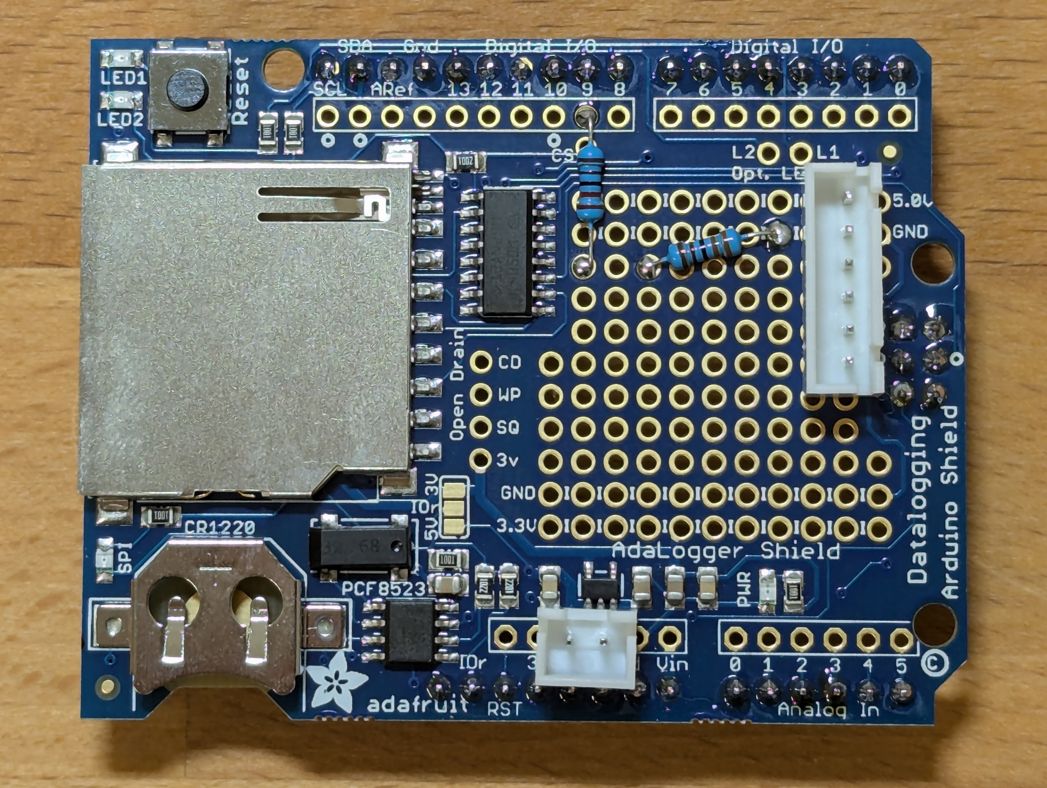
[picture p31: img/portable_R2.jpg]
portable_R2


### Step 1.3: Connecting Everything

With the connectors and resistors soldered, it is time to connect everything with short bits of wire. The general process for this is to cut an appropriate length of wire, strip the ends, pre-tin them and then solder the wire ends to the appropriate holes or pins.

The required connections are shown in the photo below. It helps to use differently coloured wires to keep a better overview of what needs to be connected where (plus it looks neat).

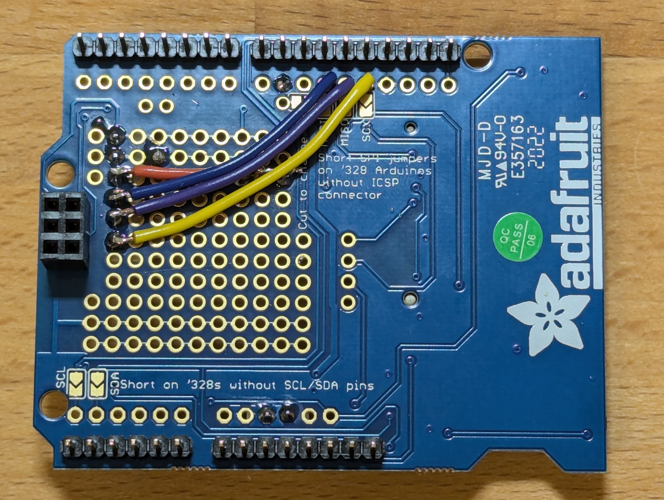
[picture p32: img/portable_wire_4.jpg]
portable_wire_4


- For the first connection, prepare a short piece of wire and solder it as shown in the photo below. Note that is soldered to **both** resistors.

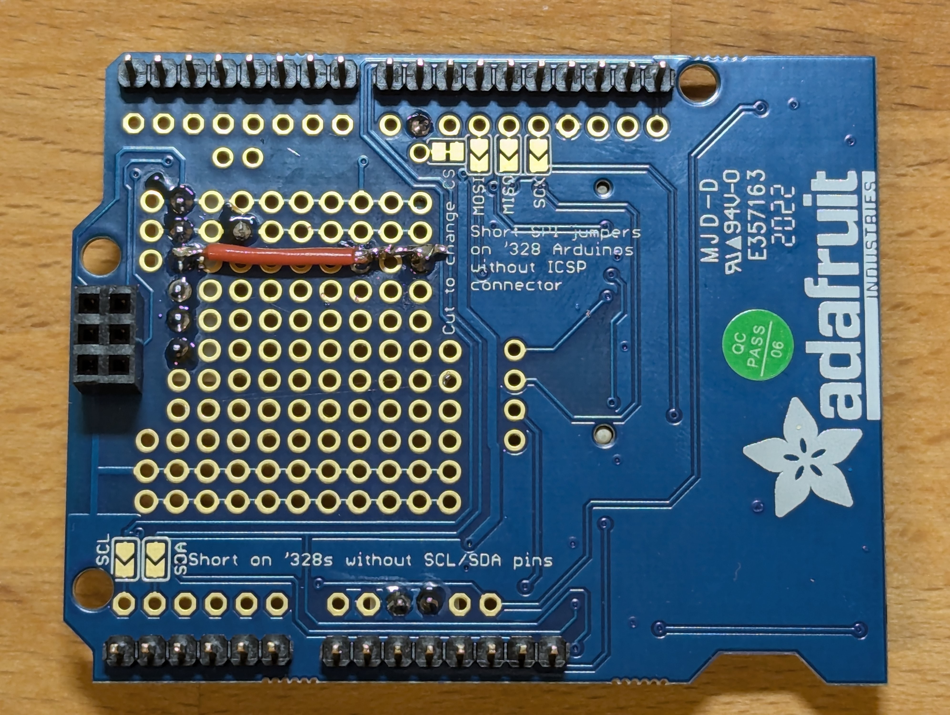
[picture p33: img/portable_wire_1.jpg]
portable_wire_1


For the following connections, bend one end of the prepared wires as shown in the photo below. These can be pushed through the holes on the DLS like the legs of connectors or resistors.

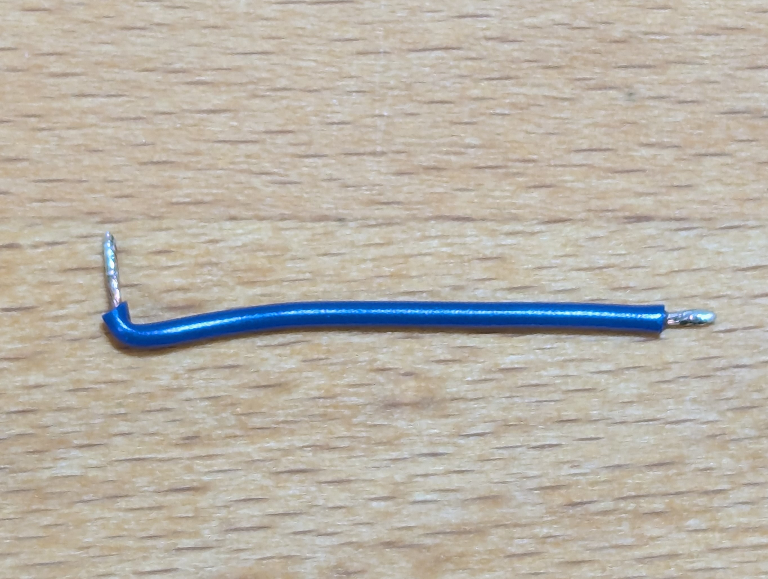
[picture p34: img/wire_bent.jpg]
wire_bent


- Next, connect the blue, purple and yellow wires as shown in the photos below.

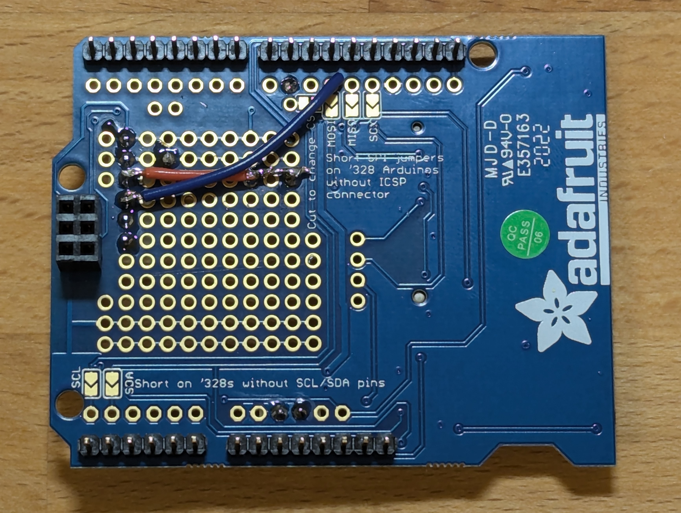
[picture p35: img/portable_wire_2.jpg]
portable_wire_2


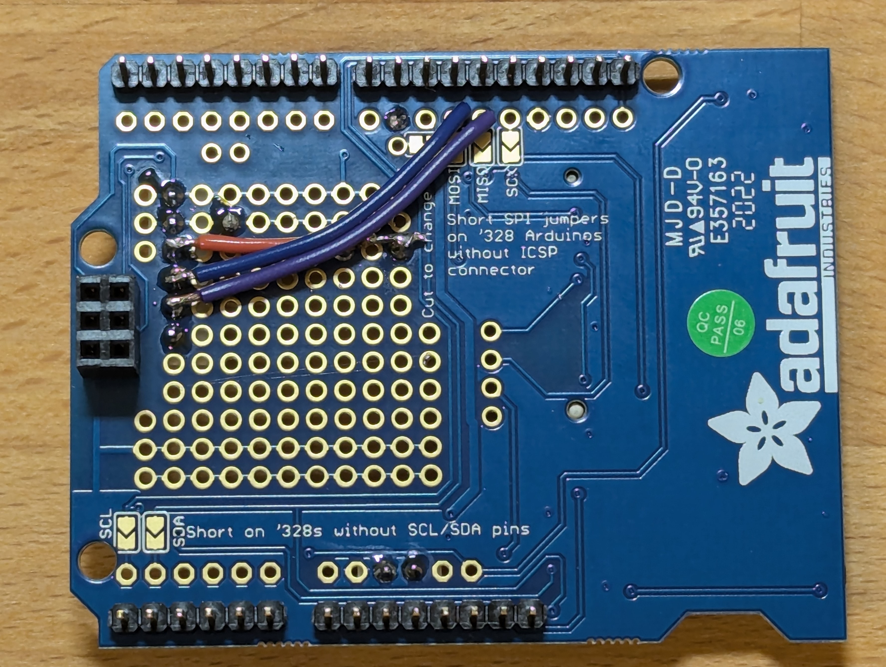
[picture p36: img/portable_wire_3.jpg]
portable_wire_3


portable_wire_4

With all the wires soldered it is a good idea to use a multimeter to check all connections are working and no pins are shorted together.

### Step 1.4: Connecting the LEDs (optional)

In this optional step, the two status LEDs on the DLS are connected.

- Connect the holes labeled `L1` and `L2` to holes `3` and `4` respectively, as shown in the schematic below. This can either be done by two _very_ short bits of wire or more easily by using bits of the resistors' trimmed off legs. You can do the connection on either side of the DLS. The easiest way to solder these connections is to fill the holes on the DLS with solder and then hold the wire/leg in place with a pair of pliers while soldering.

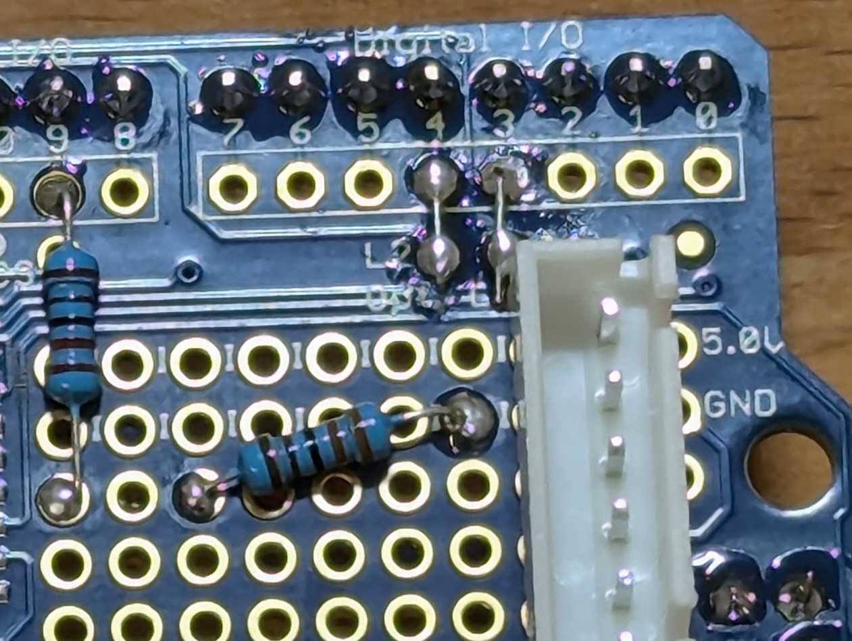
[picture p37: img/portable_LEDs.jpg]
portable_LEDs


Your DLS is now complete and should look like the one in the photos below.

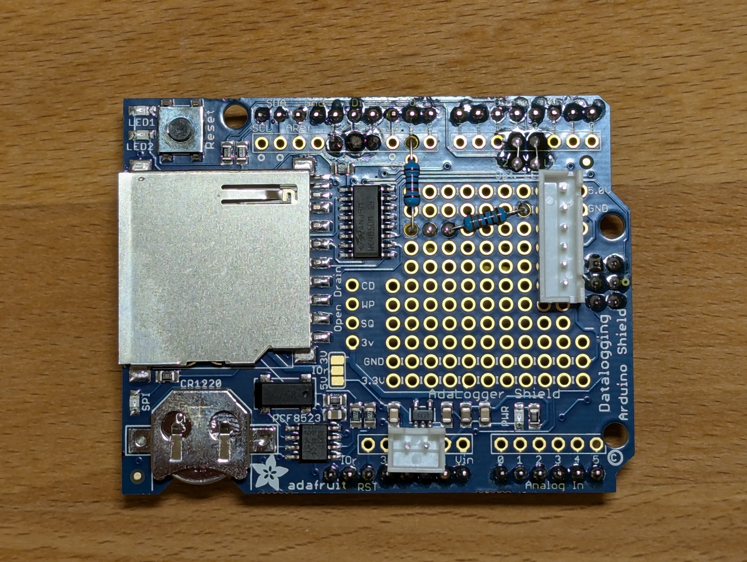
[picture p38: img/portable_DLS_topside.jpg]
portable_DLS_topside


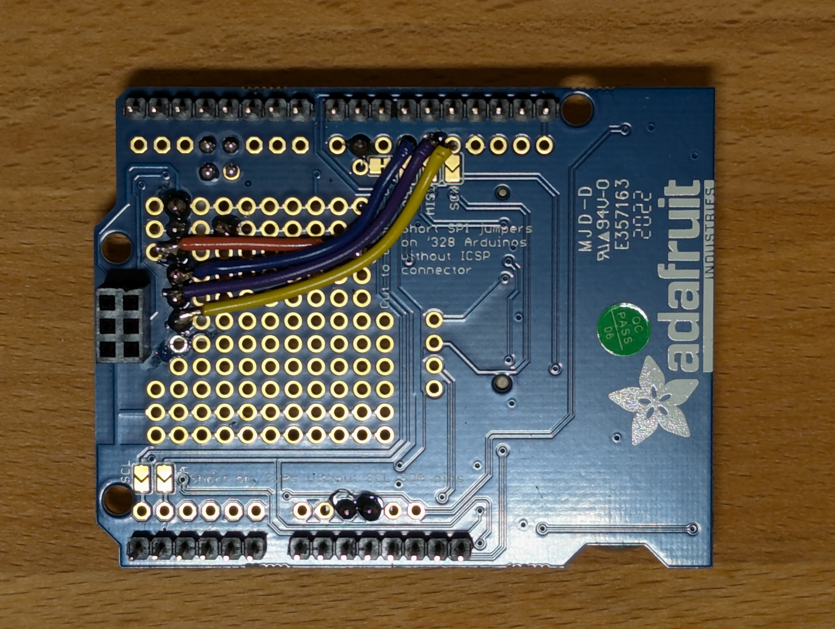
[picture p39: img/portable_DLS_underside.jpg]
portable_DLS_underside


## Step 2: Preparing the USB Power Cable

- For the USB power cable, trim off the USB Type-A end of an old USB cable. The length of this is dependant on the location and orientation of the components in your chosen housing. If the cable is too short you can lengthen it by soldering on lengths of additional wire.

- Strip the cut end of the USB cable to expose the individual wires inside. You should see four wires: white, green, red and black.

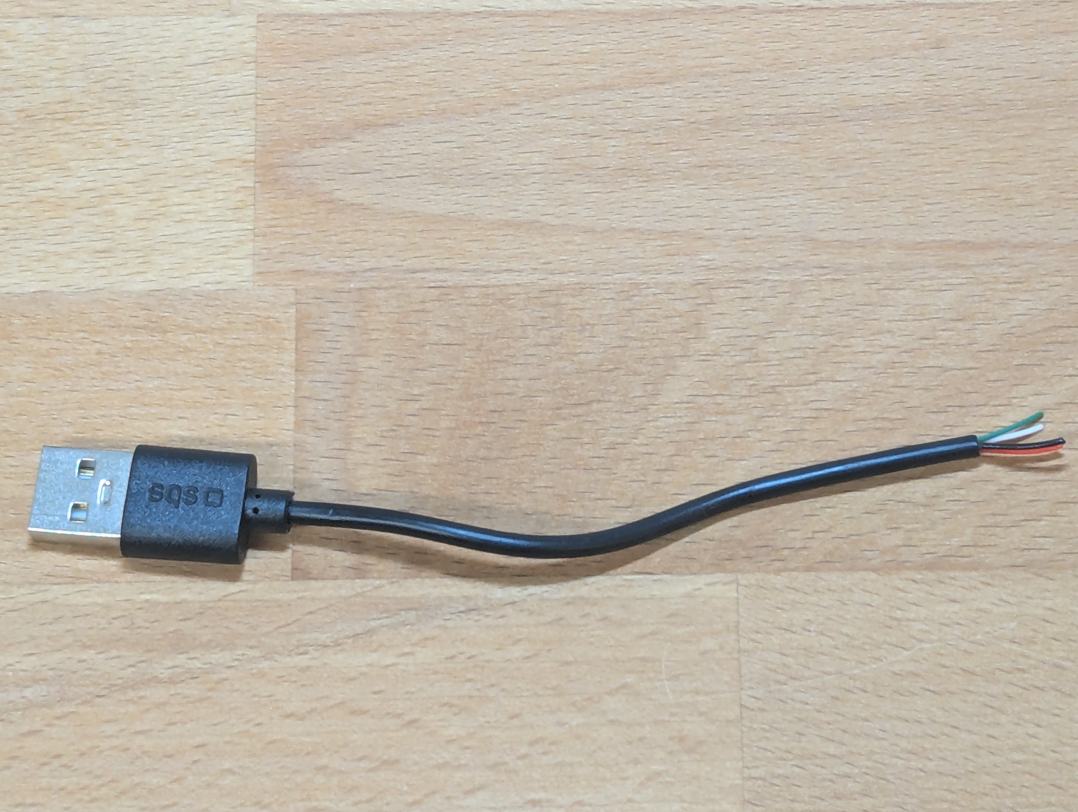
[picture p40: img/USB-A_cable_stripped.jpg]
USB-A_cable_stripped


- Trim the white and green wires  so they are flush with the insulation of the whole cable.

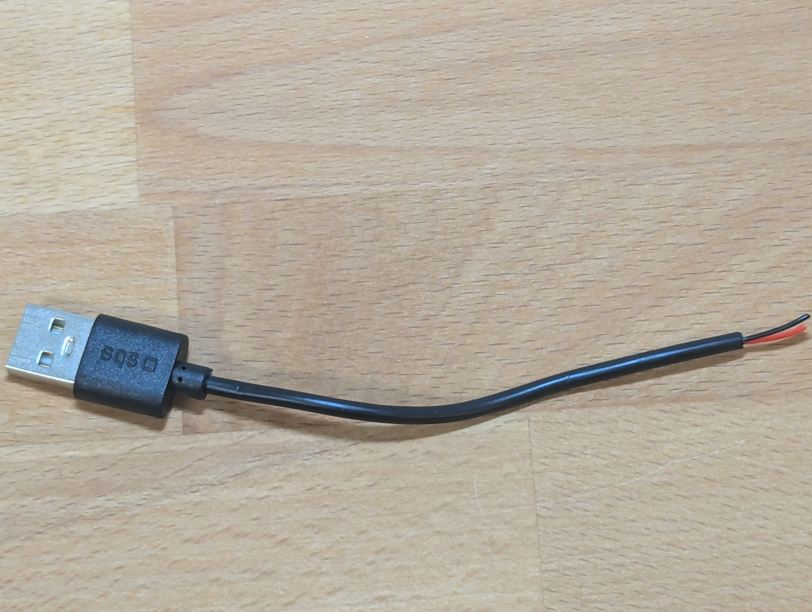
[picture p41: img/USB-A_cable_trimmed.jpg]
USB-A_cable_trimmed


- Strip the red and black wires of the USB cable and crimp on the JST connector pins. Then insert the pins into the connector in the orientation shown in the photo below. Note that the clasp side of the JST connector is facing the camera.

JST_power_orientation

If you decide to use the 3D-printable housing files provided in this repository, you will have to remove the shell of the USB Type-A connector to make the cable fit. You can do this by carefully cutting throught the plastic of the connector housing and peeling it away. You might also have to remove some of the sheet metal connector housing underneath. You should end up with a cable as shown in the photo below.

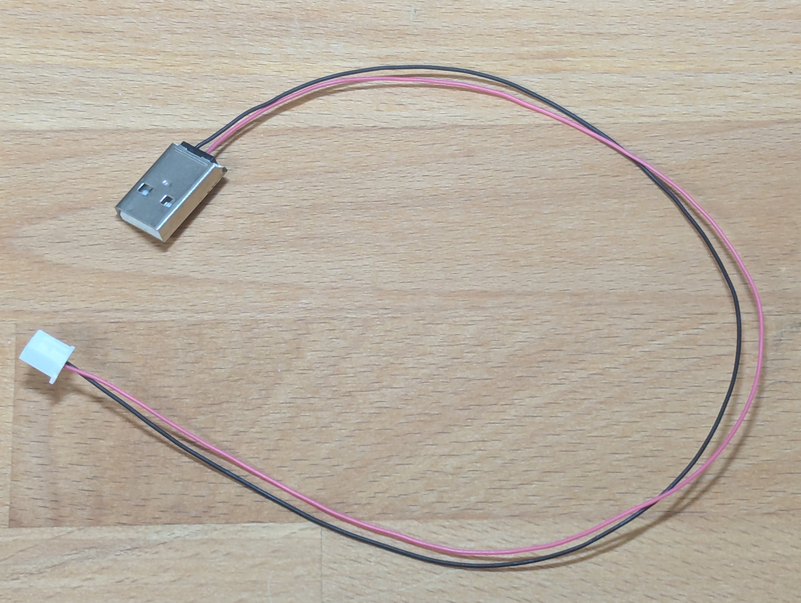
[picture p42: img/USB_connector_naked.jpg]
USB_connector_naked


## Step 3: Preparing the OPC Cable

- Take the pre-crimped Pico-Clasp cable and crimp JST connector pins on the free ends of the wires.

- Push the JST connector pins into the JST connector housing by matching the wires according to the two following Tables. Note that the clasp side of the connectors is facing the camera and that the numbering of the pins is from left to right.

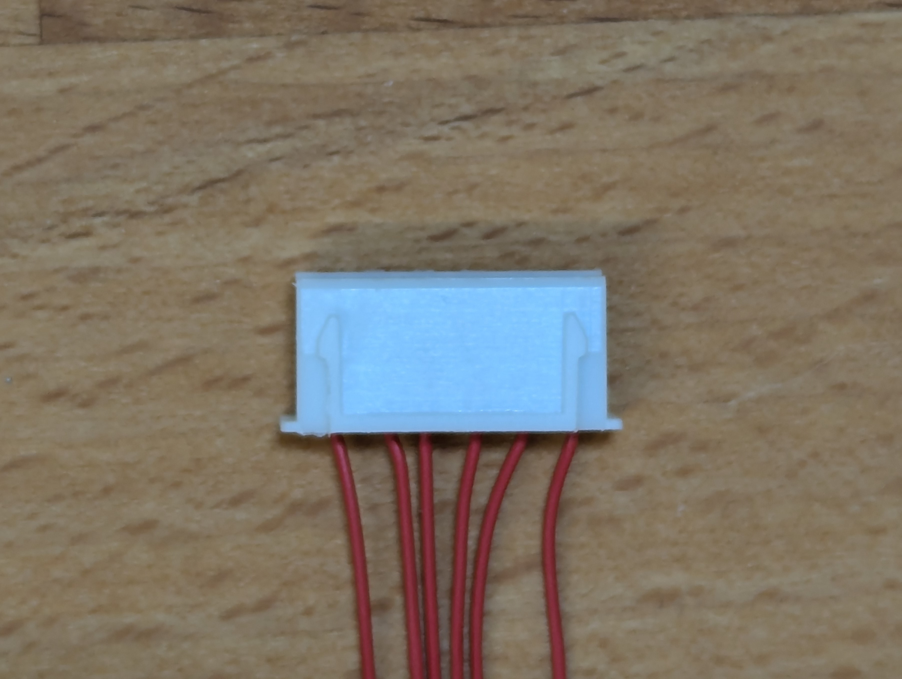
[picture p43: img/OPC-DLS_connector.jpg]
OPC-DLS_connector


#### DLS side connector wire order.

| Pin | Wire   |
| --- | ------ |
| 1   | `5.0V` |
| 2   | `GND`  |
| 3   | `DATA` |
| 4   | `MOSI` |
| 5   | `MISO` |
| 6   | `SCK`  |

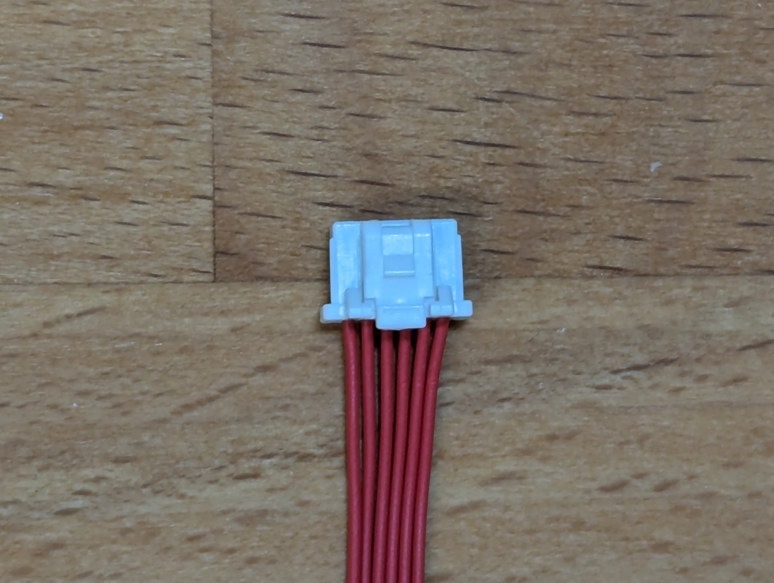
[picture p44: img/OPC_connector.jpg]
OPC_connector


#### OPC side connector wire order.

| Pin | Wire   |
| --- | ------ |
| 1   | `5.0V` |
| 2   | `SCK`  |
| 3   | `MISO` |
| 4   | `MOSI` |
| 5   | `DATA` |
| 6   | `GND`  |

## Step 4: Putting It All Together

- With the DLS, power cable and OPC cable prepared, take the Arduino UNO and place the DLS on top. Make sure to line up all of the headers correctly and carefully push the DLS down onto the UNO.

- Next, insert a CR1220 button cell battery and the SD card into their slots on the DLS and connect the OPC using the 6 pin connector and OPC cable.

If you printed the housings, it might be easier to screw the UNO onto its mountng spots before putting the DLS on top and to screw in the OPC before connecting its cable to the DLS.

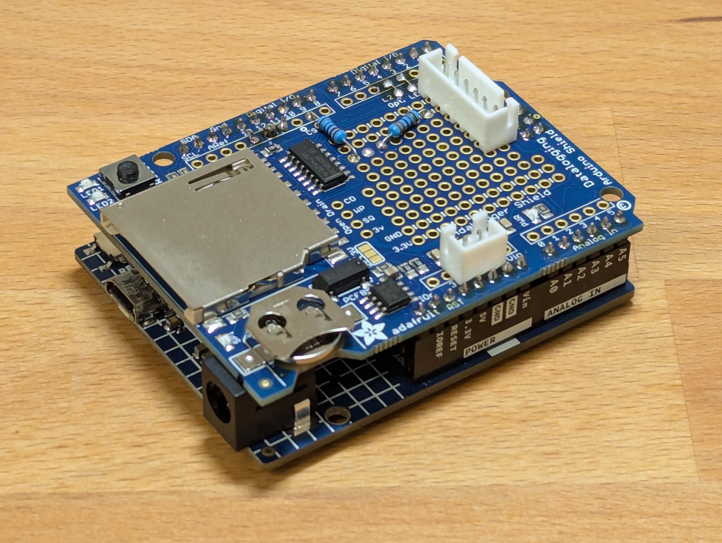
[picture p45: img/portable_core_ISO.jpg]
portable_core_ISO


Congratulations, the core of your portable PM monitor is now fully assembled! Next, keep following the steps below to get it ready for using.

## Step 5: Adjusting the RTC

To adjust the RTC on the DLS follow the steps outlined below.The OPC and SD card may be connected for this but don't have to be.

- Start the Arduino IDE on your PC

- Connect the UNO to you PC. Make sure the coin battery is properly inserted into the holder on the DLS. before doing so

- Upload the file `RTC_adjust.ino` to the UNO and let it run for at east a few seconds. You should see the current time and date being echoed to the serial monitor.

- Do not disconnect the UNO from your PC until you have completed `Step 6`! If you do, the timestamps will be wrong.

## Step 6: Uploading the Firmware

- Upload the file `Portable.ino` to the UNO

Phew, you made it! Your portable PM monitor is now ready to start collecting measurements. Have a look at the [`usage guide`](portable_usage.md) to help you with this.

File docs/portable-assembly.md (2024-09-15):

# Assembly of the Portable Monitor Core

The assembly of the portable monitor core is fairly simple thanks to the Adafruit DLS. Only basic soldering skills and a bit of wire crimping are required to complete it.

portable_core_ISO

#### Parts List

| Item                    | Value/note              | Quantity              |
| ----------------------- | ----------------------- | :-------------------: |
| Arduino UNO             | R3/R4 Minima            | 1                     |
| Adafruit DLS            | Rev. C                  | 1                     |
| Headers for DLS         | included w/ DLS         | 1 complete set        |
| Wire-to-board connector | 2 pin                   | 1 set (male & female) |
| Wire-to-board connector | 6 pin                   | 1 set (male & female) |
| USB cable               | type matching powerbank | 1                     |
| OPC connector/cable     | 6 pin Molex Pico-Clasp  | 1 (male)              |
| Resistor                | 2'200 $\Omega$          | 1                     |
| Resistor                | 3'300 $\Omega$          | 1                     |
| Wire                    | 0.25 $\textrm{mm}^2$    | 4 colours             |
| CR1220 battery          | -                       | 1                     |
| SD card                 | max. 32 GB              | 1                     |

- For the wire-to-board connectors on the DLS, any type with a pitch of ~2.5 mm works, JST XH connectors are a good choice as they are pretty resistant aginst pull out and fairly compact. Alternatively, the wires _could_ be soldered directly to the DLS, skipping the use of connectores, however this is not recommended as it makes swapping any component a lot more work.

JST_connectors

- For the OPC you need a 6 pin Molex Pico-Clasp connector. This is a _tiny_ connector and you should ideally use a special (and expensive) crimping tool to properly crimp these pins. It is easier to buy a [pre-crimped cable](https://www.aliexpress.com/item/1005005897060590.html) set which already has the connector on one side.

Pico-Clasp_connector

### Required Tools

- Soldering iron
- Solder (ideally lead-free)
- PPE (safety glasses/goggles and mask/respirator)
- Wire cutters
- Wire strippers
- Crimping tool (appropriate version for the chosen connectors)

Additionally, a soldering stand (third hand) is really helpful but not absolutely necessary.

## Step 1: Assembling RTC Shield

As the first step, the DLS is populated with all the required components and connectors.  

### Step 1.0: Installing DLS Headers

This step is only required if you bought a DLS that does not have the headers installed yet. For this step, follow the step `Installing the Headers` in [Adafruit's DLS manual](https://cdn-learn.adafruit.com/downloads/pdf/adafruit-data-logger-shield.pdf).

### Step 1.1: Soldering the Power and OPC Connectors

In this step, the 2 pin power connector and 6 pin connector for the OPC are soldered onto the DLS. 

- First, position the 2 pin power connector as shown in the photo below in the holes labeled `5v` and `GND` and take note of its orientation. 

portable_power_connector

- If you're using JST XH connectors you might have to trim a little bit of the plastic housing to clear the tips of the headers on the outside. Do this _very carefully_ with a sharp hobby knife.

JST_trimmed

- Once the header is positioned, solder it from the underside, ensuring that the pins are not shorted.

- Next, position the 6 pin OPC connector as shown in the photo below. Note that it is positioned so that the two pins towards the edge are on the rows labeled `5.0V` and `GND` and how it is orientated.

portable_OPC_connector

- Again, solder this from the underside, ensuring that no two adjacent pins are shorted.

### Step 1.2: Soldering the Resistors

In this step, the two resistors for the OPC voltage divider are soldered onto the DLS.

- First, take the `2'200 ohm` resistor and bend its legs so that it fits into the holes as shown in the image below.
portable_R1

- Once positioned correctly, solder the resistor from the underside and trim the legs.

- For the `3'300 ohm` resistor, position it as shown in the schematic below and repeat the same process as for the first resistor.

portable_R2

### Step 1.3: Connecting Everything

With the connectors and resistors soldered, it is time to connect everything with short bits of wire. The general process for this is to cut an appropriate length of wire, strip the ends, pre-tin them and then solder the wire ends to the appropriate holes or pins.

The required connections are shown in the image below. It helps to use differently coloured wires to keep a better overview of what needs to be connected where (plus it looks neat).

--TODO IMAGE_PORTABLE_CORE_SCHEMATIC_WIRE_CONNECTONS_UNDERSIDE

--TODO describe/tips for each connection

Your DLS should now look like the one in the image below.

--TODO IMAGE_PORTABLE_CORE_WIRE_CONNECTIONS_SOLDERED_UNDERSIDE

### Step 1.4: Connecting the LEDs (optional)

In this optional step, the two status LEDs on the DLS are connected.

- Connect the holes labeled `L1` and `L2` to holes `3` and `4` respectively, as shown in the schematic below. This can either be done by two _very_ short bits of wire or more easily by using bits of the resistors' trimmed off legs. You can do the connection on either side of the DLS.

--TODO IMAGE_PORTABLE_CORE_SCHEMATIC_LED_CONNECTIONS

--TODO IMAGE_PORTABLE_SCORE_LED_CONNECTIONS_SOLDERED

Your DLS is now complete and should look like the one in the images below.

portable_DLS_topside

portable_DLS_underside

## Step 2: Preparing the (USB) Power Cable

--TODO instructions for making USB power cable

## Step 3: Preparing the OPC Cable

--TODO instructions for making OPC cable

## Step 4: Putting It All Together

With the DLS, power cable and OPC cable prepared, take the Arduino UNO and place the DLS on top. Make sure to line up all of the headers correctly and carefully push the DLS down onto the UNO. Next, insert a CR1220 button cell battery and the SD card into their slots on the DLS and connect the OPC using the 6 pin connector and OPC cable.

If you printed the housings, it might be easier to screw the UNO onto its mountng spots before putting the DLS on top and to screw in the OPC before connecting its cable to the DLS.

Congratulations, the core of your portable PM monitor is now fully assembled! Next, have a look at --TODO LINK_FIRMWARE_UPLOAD to finish the monitor by uploading the firmware.

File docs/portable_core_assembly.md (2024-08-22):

# Assembly of the portable monitor core

The assembly of the portable monitor core is fairly simple thanks to the Adafruit DLS. Only basic soldering skills and a bit of wire crimping are required to complete it.

--TODO IMAGE_PORTABLE_CORE_OVERVIEW

### Parts list

| Item                     | Value/note             | Qty                   |
| ------------------------ | ---------------------- | :-------------------: |
| Arduino UNO              | R3/R4 Minima           | 1                     |
| Adafruit DLS             | Rev. C                 | 1                     |
| Headers for DLS          | included w/ DLS        | 1 complete set        |
| Connector                | 2 pin                  | 1 set (male & female) |
| Connector                | 6 pin                  | 1 set (male & female) |
| OPC connector/cable      | 6 pin Molex Pico-Clasp | 1 (male)              |
| Resistor                 | VALUE_1                | 1                     |
| Resistor                 | VALUE_2                | 1                     |
| Wire                     | GAUGE                  | ? colours             |
| CR1220 battery           | -                      | 1                     |
| SD card                  | max. 32 GB             | 1                     |

- For the connectors on the DLS, any type with a pitch of ~2.5 mm works, JST XH connectors are a good choice as they are pretty resistant aginst pull out and fairly compact. Alternatively, the wires _could_ be soldered directly to the DLS, skipping the use of connectores, however this is not recommended as it makes swapping any component a lot more work.

--TODO IMAGE_JST_CONNECTOR_2_AND_6_PIN

- For the OPC you need a 6 pin Molex Pico-Clasp connector. This is a _tiny_ connector and you should ideally use a special (and expensive) crimping tool to properly crimp these pins. It is easier to buy a pre-crimped cable set which already has the connector on one side (--TODO ADD_EXAMPLE_LINK).

--TODO IMAGE_OPC_CABLE_BLANK

### Required tools

- Soldering iron
- Solder (ideally lead-free)
- PPE (safety glasses/goggles and mask/respirator)
- Wire cutters
- Wire strippers
- Crimping tool (appropriate version for the chosen connectors)

Additionally, a soldering stand (third hand) is really helpful but not absolutely necessary.

## Step 1: Assembling RTC shield

As the first step, the DLS is populated with all the required components and connectors. 

--TODO IMAGE_DLS_EMPTY_WITH_HEADERS_ISO_VIEW

### Step 1.0: Installing DLS headers

This step is only required if you bought a DLS that does not have the headers installed yet. For this step, follow the step `Installing the Headers` in [Adafruit's DLS manual](https://cdn-learn.adafruit.com/downloads/pdf/adafruit-data-logger-shield.pdf).

### Step 1.1: Soldering the power and OPC connectors

In this step, the 2 pin power connector and 6 pin connector for the OPC are soldered onto the DLS. 

- First, position the 2 pin power connector as shown in the schematic below in the holes labeled `Vin` and `GND` and take note of its orientation. 

--TODO IMAGE_PORTABLE_CORE_SCHEMATIC_PWR_CONNECTOR

- If you're using JST XH connectors you might have to trim a little bit of the plastic housing to clear the tips of the headers on the outside. Do this _very carefully_ with a sharp hobby knife.

--TODO IMAGE_JST_INTERFERENCE_TRIMMED

- Once the header is positioned, solder it from the underside, ensuring that no two adjacent pins are shorted.

--TODO IMAGE_PORTABLE_CORE_SCHEMATIC_PWR_CONNECTOR_SOLDERED_UNDERSIDE

- Next, position the 6 pin OPC connector as shown in the schematic below. Note that it is positioned so that the two pins towards the edge are on the rows labeled `5.0V` and `GND` and how it is orientated.

--TODO IMAGE_PORTABLE_CORE_SCHEMATIC_OPC_CONNECTOR

- Again, solder this from the underside, ensuring that no two adjacent pins are shorted.

Your DLS should now look like the one in the image below.

--TODO IMAGE_PORTABLE_CORE_CONNECTORS_SOLDERED_TOPSIDE

### Step 1.2: Soldering the resistors

In this step, the two resistors for the OPC voltage divider are soldered onto the DLS.

- First, take the `VALUE_1` resistor and bend its legs so that it fits into the holes as shown in the image below.

--TODO IMAGE_PORTABLE_CORE_SCHEMATIC_VALUE_1_RESISTOR

- Once positioned correctly, solder the resistor from the underside and trim the legs.

--TODO IMAGE_PORTABLE_CORE_RESISTOR_SOLDERED_UNDERSIDE

- For the `VALUE_2` resistor, position it as shown in the schematic below and repeat the same process as for the first resistor.

--TODO IMAGE_PORTABLE_CORE_SCHEMATIC_VALE_2_RESISTOR

Your DLS should now look like the one in the image below.

--TODO IMAGE_PORTABLE_CORE_CONNECTORS_RESISTORS_SOLDERED_TOPSIDE

--TODO IMAGE_PORTABLE_CORE_CONNECTORS_RESISTORS_SOLDERED_UNDERSIDE

### Step 1.3: Connecting everything

With the connectors and resistors soldered, it is time to connect everything with short bits of wire. The general process for this is to cut an appropriate length of wire, strip the ends, pre-tin them and then solder the wire ends to the appropriate holes or pins.

The required connections are shown in the image below. It helps to use differently coloured wires to keep a better overview of what needs to be connected where (plus it looks neat).

--TODO IMAGE_PORTABLE_CORE_SCHEMATIC_WIRE_CONNECTONS_UNDERSIDE

--TODO describe/tips for each connection

Your DLS should now look like the one in the image below.

--TODO IMAGE_PORTABLE_CORE_WIRE_CONNECTIONS_SOLDERED_UNDERSIDE

### Step 1.4: Connecting the LEDs (optional)

In this optional step, the two status LEDs on the DLS are connected.

- Connect the holes labeled `L1` and `L2` to holes `3` and `4` respectively, as shown in the schematic below. This can either be done by two _very_ short bits of wire or more easily by using bits of the resistors' trimmed off legs. You can do the connection on either side of the DLS.

--TODO IMAGE_PORTABLE_CORE_SCHEMATIC_LED_CONNECTIONS

--TODO IMAGE_PORTABLE_SCORE_LED_CONNECTIONS_SOLDERED

## Step 2: Preparing the (USB) power cable

--TODO instructions for making USB power cable

## Step 3: Preparing the OPC cable

--TODO instructions for making OPC cable

## Step 4: Putting it all together

With the DLS, power cable and OPC cable prepared, take the Arduino UNO and place the DLS on top. Make sure to line up all of the headers correctly and carefully push the DLS down onto the UNO. Next, insert a CR1220 button cell battery and the SD card into their slots on the DLS and connect the OPC using the 6 pin connector and OPC cable.

If you printed the housings, it might be easier to screw the UNO onto its mountng spots before putting the DLS on top and to screw in the OPC before connecting its cable to the DLS.

Congratulations, the core of your portable PM monitor is now fully assembled! Next, have a look at --TODO LINK_FIRMWARE_UPLOAD to finish the monitor by uploading the firmware.

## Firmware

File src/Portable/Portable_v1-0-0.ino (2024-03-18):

/* --------------------
Portable
v1-0-0

Code for the Arduino of the portable monitor. Check the README file for documentation.
-------------------- */


/* -------- Libraries & definitions -------- */


#include <SPI.h> // CHECK LICENSE
#include <SD.h> // CHECK LICENSE
#include <RTClib.h> // CHECK LICENSE

// Pins for SPI
#define SPI_SCK 13 // Clock
#define SPI_SDI 12 // SDI
#define SPI_SDO 11 // SDO

// SPI chipselect pins
#define SPI_OPC_CS 9
#define SPI_DLS_CS 10

// OPC status bytes
#define OPC_busy 0x31
#define OPC_ready 0xF3

// Pins for external status LEDs
#define GreenLED 3
#define RedLED 4


/* -------- User parameters -------- */


unsigned int MeasInterval = 10000; // Measurement interval in (ms)
unsigned long Timeout = 1000; // Timeout in (ms)

String FileExtension = ".csv"; // File extension of the local save file (.csv or .txt)


/* -------- Variables -------- */


struct OPCData // Struct for storing the data from the OPC
{
  String MeasDate;
  String MeasTime;

  uint16_t BinCount[24];

  float SamplingPeriod;
  float SampleFlowRate;
  float Temperature;
  float Humidity;

  float PMA;
  float PMB;
  float PMC;

  uint16_t LaserStatus; // Laser status of the OPC, 550 < LaserStatus < 650 during normal operation

  uint16_t ChecksumReceived;
  uint16_t ChecksumCalculated;
  bool ChecksumMatch;
};

// SPI buffer for reading data from the OPC.
unsigned char SPI_Buffer[86];
unsigned int SPI_Buffer_Index;

unsigned long CurrentTime;
unsigned long NextMeas;

unsigned long RetryTimer = 0;

bool FirstMeas; // Used to discard the first set of measurements


RTC_PCF8523 RTC;
DateTime Now;

String Filename;

OPCData Data;


/* -------- Setup -------- */


void setup()
{
  Serial.begin(9600);

  delay(2000);

  // Configure LED pins
  pinMode(GreenLED, OUTPUT);
  pinMode(RedLED, OUTPUT);
  SetLED(GreenLED, LOW);
  SetLED(RedLED, HIGH);

  // Configure SPI CS pins
  pinMode(SPI_OPC_CS, OUTPUT);
  pinMode(SPI_DLS_CS, OUTPUT);
  SetCS(SPI_OPC_CS, HIGH);
  SetCS(SPI_DLS_CS, HIGH); 

  delay(2000);

  SPI.begin();

  // Start all devices
  StartRTC();
  Serial.println("RTC started!");
  StartSD();
  Serial.println("SD started!");
  CreateSDFile();
  Serial.println("SD file started!");
  StartOPC();
  Serial.println("OPC started!");

  CurrentTime = millis();
  NextMeas = CurrentTime;

  SetLED(GreenLED, HIGH);
  delay(1000);
  SetLED(RedLED, LOW);
}


/* -------- Main loop -------- */


void loop()
{
  CurrentTime = millis();

  if (CurrentTime >= NextMeas)
  {
    NextMeas = CurrentTime + MeasInterval;

    Data = ReadOPCData();

    if (FirstMeas == false)
    {
      SaveSDData(Data, Filename);
    }
    else
    {
      FirstMeas == false;
    }
  }

}


/* -------- RTC functions -------- */


void StartRTC (void) // Start the RTC.
{
  RetryTimer = 0; // Reset the timeout timer to 0.

  while (!RTC.begin()) // Try starting the RTC.
  {
    RetryTimer += 200; // Increase the timeout timer.

    if (RetryTimer >= Timeout) // Error out if the RTC doesn't start within Timeout (if this happens, check the DLS/RTC).
    {
      HardError();
    }

    delay(200); // Wait 200 ms and try again
  }

  delay(2000); // Wait 2 seconds for the PCF8523's crystal oscillator to stabilise.

  RTC.start(); // Clear the stop bit of the RTC.
  
  return;
}


/* -------- SD card functions -------- */


void StartSD (void) // Start communication with the SD card
{
  RetryTimer = 0;

  while (!SD.begin(SPI_DLS_CS)) // Try starting communication with the SD card
  {
    RetryTimer += 200;

    if (RetryTimer >= Timeout) // Error out if communication doesn't start within Timeout 
    {
      HardError();
    }

    delay(200); // Wait 200 ms and try again
  }
}


void CreateSDFile (void) // Create a new file on the SD card and write the file header to it
{
  Now = RTC.now(); // Get the current date & time from the RTC

  char NameFormat[] = "DDhhmmss"; // Filename will be DDHHMMSS.ext
  Filename = (Now.toString(NameFormat) + FileExtension);

  if (SD.exists(Filename)) // Check if a file with this name already exists and halt if this is the case
  {
    HardError();
  }

  File DataFile = SD.open(Filename, FILE_WRITE); // Open the file

  if (DataFile) // Write the file header to the file
  {
    DataFile.print(F("date,time")); // Date & time

    for (int i = 0; i < 24; i++) // Add a leading 0 for single digit bin numbers
    {
      DataFile.print(",bin");

      if (i < 10)
      {
        DataFile.print(0);
      }

      DataFile.print(i); // Bin number
    }

    DataFile.println(",SP(s),SFR(ml/s),T(C),RH(%),PM_A(ug/m^3),PM_B(ug/m^3),PM_C(ug/m^3),CSmatch"); // Other columns

    DataFile.close();
  }
  else
  {
    HardError();
  }
}


void SaveSDData (OPCData Data, String SaveFile) // Save the data from the struct Data to the file SaveFile
{
  if (SD.exists(SaveFile)) // Check if the file exists
  {
    File DataFile = SD.open(SaveFile, FILE_WRITE);

    if (DataFile) // Write the data to the file
    {
      DataFile.print(Data.MeasDate);
      AddSep(DataFile);
      DataFile.print(Data.MeasTime);
      AddSep(DataFile);

      for (int i = 0; i < 24; i++) // Save the BinCounts to the file
      {
        DataFile.print(Data.BinCount[i]);
        AddSep(DataFile);
      }

      DataFile.print(Data.SamplingPeriod);
      AddSep(DataFile);
      DataFile.print(Data.SampleFlowRate);
      AddSep(DataFile);
      DataFile.print(Data.Temperature);
      AddSep(DataFile);
      DataFile.print(Data.Humidity);
      AddSep(DataFile);

      DataFile.print(Data.PMA);
      AddSep(DataFile);
      DataFile.print(Data.PMB);
      AddSep(DataFile);
      DataFile.print(Data.PMC);
      AddSep(DataFile);

      DataFile.println(Data.ChecksumMatch);

      DataFile.close();
    }
    else
    {
      HardError();
    }
  }
  else
  {
    HardError();
  }
}


void AddSep (File OutFile) // Print a column seperator to the file OutFile
{
  OutFile.print(",");
}


/* -------------------- OPC Functions -------------------- */


void StartOPC (void) //--TODO
{
  // Start the laser
  QueryOPC(0x03);
  SPI.transfer(0x07);
  SetCS(SPI_OPC_CS, LOW);
  SPI.endTransaction();
  delay(1000);

  // Start the fan and wait for it to spin up
  QueryOPC(0x03);
  SPI.transfer(0x03);
  SetCS(SPI_OPC_CS, LOW);
  SPI.endTransaction();
  delay(5000);
}


OPCData ReadOPCData (void) //--TODO add comments
{
  OPCData NewData;
  Now = RTC.now(); // Get the timestamp for the current measurement

  QueryOPC(0x30);

  // Read the full histogram from the OPC
  for (SPI_Buffer_Index = 0; SPI_Buffer_Index < 86; SPI_Buffer_Index++)
  {
    delayMicroseconds(10);
    SPI_Buffer[SPI_Buffer_Index] = SPI.transfer(0x01);
  }

  SetCS(SPI_OPC_CS, HIGH);
  SPI.endTransaction();

  // Transfer the histogram data from the SPI_Buffer to the NewData struct
  unsigned int BinIndex = 0; // Index for the 24 bins
  uint16_t *pUInt16; // Pointer to unisgned int values
  uint16_t ConvInt; // Used to temporarilly store the unsigned int values
  float *pFloat; // Pointer to float values

  char DateFormat[] = "YYYY-MM-DD"; // Date format
  char TimeFormat[] = "hh:mm:ss"; // Time format

  // Transfer/convert the data from the SPI_Buffer to the NewData struct

  // Time & date
  NewData.MeasDate = Now.toString(DateFormat);
  NewData.MeasTime = Now.toString(TimeFormat);

  // Bin counts for all 24 bins
  for (SPI_Buffer_Index = 0; SPI_Buffer_Index < 48; SPI_Buffer_Index += 2)
  {
    pUInt16 = (uint16_t *)&SPI_Buffer[SPI_Buffer_Index];
    NewData.BinCount[BinIndex] = *pUInt16;

    BinIndex++;
  }

  // Sampling period
  pUInt16 = (uint16_t *)&SPI_Buffer[52];
  ConvInt = *pUInt16;
  NewData.SamplingPeriod = (float)ConvInt/100;

  // Sample flow rate
  pUInt16 = (uint16_t *)&SPI_Buffer[54];
  ConvInt = *pUInt16;;
  NewData.SampleFlowRate = (float)ConvInt/100;

  // Temperature
  pUInt16 = (uint16_t *)&SPI_Buffer[56];
  ConvInt = *pUInt16;
  NewData.Temperature = -45 + 175*(float)ConvInt/65535;

  // Relative Humidity
  pUInt16 = (uint16_t *)&SPI_Buffer[58];
  ConvInt = *pUInt16;
  NewData.Humidity = 100*(float)ConvInt/65535;

  // PM_A
  pFloat = (float *)&SPI_Buffer[60];
  NewData.PMA = *pFloat;
  // PM_B
  pFloat = (float *)&SPI_Buffer[64];
  NewData.PMB = *pFloat;
  // PM_C
  pFloat = (float *)&SPI_Buffer[68];
  NewData.PMC = *pFloat;

  // Laser status
  pUInt16 = (uint16_t *)&SPI_Buffer[82];
  NewData.LaserStatus = *pUInt16;

  // Checksums and comparison
  pUInt16 = (uint16_t *)&SPI_Buffer[84];
  NewData.ChecksumReceived = *pUInt16;

  NewData.ChecksumCalculated = ChecksumCalc(SPI_Buffer, 84); // Calculate the checksum from the received data

  if (NewData.ChecksumReceived == NewData.ChecksumCalculated) // Compare the received and calculated checksums
  {
    NewData.ChecksumMatch = true;
  }
  else
  {
    NewData.ChecksumMatch = false;
  }

  return NewData;
}


void QueryOPC (unsigned char Command) // Start SPI communication with the OPC --TODO add comments/explanations
{
  unsigned char Response;
  int Tries;

  SPI.beginTransaction(SPISettings(300000, MSBFIRST, SPI_MODE1));

  Response = SPI.transfer(Command); // Read a byte to clear the OPC's SPI buffer

  delay (1);

  do
  {
    SetCS(SPI_OPC_CS, LOW);
    Tries = 0;

    do
    {
      Response = SPI.transfer(Command);

      if (Response != OPC_ready)
      {
        delay(1);
      }

      Tries++;
    }
    while ((Tries < 20) && (Response != OPC_ready));

    if (Response != OPC_ready)
    {
      if (Response == OPC_busy) // If the OPC indicates that it is busy, set the CS pin of the OPC high and wait a few seconds before trying again
      {
        SetCS(SPI_OPC_CS, HIGH);

        delay(2000);
      }
      else // If the response is neither OPC_ready nor OPC_busy, stop SPI communication and delay before trying again
      {
        SetCS(SPI_OPC_CS, HIGH);
        SPI.endTransaction();

        delay(5000);

        SPI.beginTransaction(SPISettings(300000, MSBFIRST, SPI_MODE1));
      }
    }
  }
  //while (Response != OPC_ready);
  while ((Response != OPC_ready) && (Serial.available() == 0)); //--CHECK if works with other line

  delay(10);
}


unsigned int ChecksumCalc (unsigned char SPI_Data[], unsigned char DataBytes) // Calculate the checksum from the received data --TODO add comments/explanations of how this works
{
  #define Polynom 0xA001
  #define InitVal 0xFFFF

  unsigned char _bit;
  unsigned int Checksum = InitVal;
  unsigned char Count;

  for(Count = 0; Count < DataBytes; Count++)
  {
    Checksum ^= (unsigned int)SPI_Data[Count];
    for(_bit = 0; _bit < 8; _bit++)
    {
      if (Checksum & 1)
      {
        Checksum >>= 1;
        Checksum ^= Polynom;
      }
      else
        Checksum >>= 1;
    }
  }
  return Checksum;
}


/* -------------------- Misc Functions -------------------- */


void SetLED (int Pin, bool State) // Set the LED pin Pin to state State
{
  digitalWrite(Pin, State);
}


void SetCS (int Pin, bool State) // Set the chip select pin Pin to state State
{
  digitalWrite(Pin, State);
}


void HardError (void) // Blink the red LED and halt until the Arduino is reset
{
  SetLED(GreenLED, LOW);

  while (1)
  {
    SetLED(RedLED, HIGH);
    delay(500); 
    SetLED(RedLED, LOW);
    delay(500);
  }
}


/* -------- End of file -------- */

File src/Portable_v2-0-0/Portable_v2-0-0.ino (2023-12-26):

/*
--TODO
*/


#include <SPI.h>
#include <SD.h>
#include <RTClib.h>


#define OPC_busy 0x31 // This hex value indicates that the OPC is NOT ready for SPI communication.
#define OPC_ready 0xF3 // This hex value indicates that teh OPC IS ready for SPI communication.

#define SPI_SCK 13 // SPI clock pin on Arduino UNO
#define SPI_SDI 12 // SPI SDI (MISO) pin on Arduino UNO
#define SPI_SDO 11 // SPI SDO (MOSI) pin on Arduino UNO

#define SPI_OPC_CS 9 // Chip select pin for the OPC
#define SPI_DLS_CS 10 // Chip select pin for the DLS

#define GreenLED 3 // Pin for the green LED on the DLS
#define RedLED 4 // Pin for the red LED on the DLS


unsigned char SPI_Buffer[86]; // Buffer for reading data from the OPC
unsigned int SPI_Buffer_Index; // Index for SPI_Buffer

struct OPCData // Struct for storing the data from the OPC
{
  String MeasDate; //--TODO
  String MeasTime;

  uint16_t BinCount[24]; // Sample counts for each of the 24 bins

  float SamplingPeriod; // Sampling period reported by the OPC
  float SampleFlowRate; // Sample flow rate reported by the OPC
  float Temperature; // Temperature from the OPC's temperature sensor, very inaccurate
  float Humidity; // Relative humidity from the OPC's humidity sensor, very inaccurate

  float PMA; //--TODO
  float PMB;
  float PMC;

  uint16_t LaserStatus; // Laser status of the OPC, 550 < LaserStatus < 650 during normal operation

  uint16_t ChecksumReceived; // The checksum received from the OPC
  uint16_t ChecksumCalculated; // The checksum calculated from the data in the struct
  bool ChecksumMatch; // 1 if the received and calculated checksums match, 0 otherwise
};

unsigned int MeasInterval = 10000; // The measurment interval in (ms)
unsigned long CurrentTime;
unsigned long NextMeas;

unsigned long RetryTimer = 0;
unsigned long Timeout = 1000;

bool FirstMeas; // Used to identify the first histogram read from the OPC.

RTC_PCF8523 RTC;
DateTime Now;

String Filename;
String FileExtension = ".csv";

OPCData Data;


/* -------------------- Setup & Loop -------------------- */


void setup()
{
  Serial.begin(9600);

  delay(2000);

  pinMode(GreenLED, OUTPUT);
  pinMode(RedLED, OUTPUT);
  SetLED(GreenLED, LOW);
  SetLED(RedLED, HIGH);

  pinMode(SPI_OPC_CS, OUTPUT);
  pinMode(SPI_DLS_CS, OUTPUT);
  SetCS(SPI_OPC_CS, HIGH);
  SetCS(SPI_DLS_CS, HIGH); 

  delay(2000);

  SPI.begin();

  StartRTC();
  StartSD();
  CreateSDFile();
  StartOPC();

  CurrentTime = millis();
  NextMeas = CurrentTime;

  SetLED(GreenLED, HIGH);
  delay(1000);
  SetLED(RedLED, LOW);
}


void loop()
{
  CurrentTime = millis();

  if (CurrentTime >= NextMeas)
  {
    NextMeas = CurrentTime + MeasInterval;

    Data = ReadOPCData();

    if (FirstMeas == false)
    {
      SaveSDData(Data, Filename);
    }
    else
    {
      FirstMeas == false;
    }
  }

}


/* -------------------- RTC Functions -------------------- */


void StartRTC (void) // Start the RTC and adjust it if the Arduino is connected to a PC
{
  RetryTimer = 0;

  while (!RTC.begin()) // Try starting the RTC
  {
    RetryTimer += 200;

    if (RetryTimer >= Timeout) // Error out if the RTC doesn't start within Timeout 
    {
      HardError();
    }

    delay(200); // Wait 200 ms and try again
  }

  delay(2000); // Wait 2 seconds for the PCF8523's crystal oscillator to stabilise before trying to adjust the RTC

  //RTC.adjust(DateTime(F(__DATE__), F(__TIME__)));

  RTC.start(); // Clear the stop bit of the RTC
}


/* -------------------- SD Card Functions -------------------- */
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

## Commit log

2024-08-22 Update and rename portable_core_assembly.md to portable_core-assembly.md
2024-08-22 Update and rename stationary_core_assembly.md to stationary-assembly.md
2024-09-15 Update and rename portable-assembly.md to portable_assembly.md
2024-09-15 Update and rename stationary-assembly.md to stationary_assembly.md
